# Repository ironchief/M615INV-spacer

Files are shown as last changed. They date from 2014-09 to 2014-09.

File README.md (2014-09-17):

This is a spacer for the OMAX M615INV Portable Inverted Microscope 40x-400x. ([Amazon], [MicroscopeNet])

The spacer allows tissue flasks and petri dishes to fit on the stage by increasing the distance between the light condensor and the sample stage. You can adjust the height using the OpenSCAD or the Makerbot customizer. The original height is 19mm.

---
## Parts
You can reuse the screws, washers and dowel from the original spacer or purchase additional ones with the links below.

- Washer 
    - M3 Metric DIN 125 18-8 Stainless Steel Flat Washer
    - [McMaster-Carr 93475A210](http://www.mcmaster.com/#93475a210)
- Screw
    - M3 6mm 18-8 Stainless Steel Metric Pan Head Phillips Machine Screw
    - [McMaster-Carr 92000A116](http://www.mcmaster.com/#92000a116)
- Dowel
    - M6 22mm Metric 18-8 Stainless Steel Dowel Pin
    - [McMaster-Carr 91585A161](http://www.mcmaster.com/#91585a161)

## Assembly

Loosen the screw at the base of the light source to remove it from the base. Then unscrew the two philips head screws that attach the spacer to the battery case. Reassemble with your printed spacer.

## Files
The OpenScad and STL files can be found on [Github]. Please feel free to make fixes, issues and submit pull requests.

[Amazon]: http://www.amazon.com/OMAX-40X-400X-Portable-Monocular-Microscope/dp/B004EBEYZS
[MicroscopeNet]: http://www.microscopenet.com/40x400x-portable-inverted-microscope-p-8917.html
[Github]: https://github.com/ironchief/M615INV-spacer

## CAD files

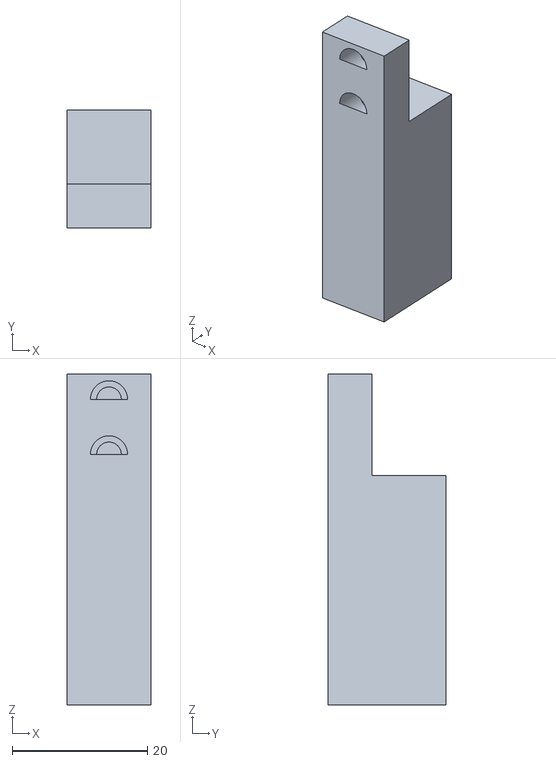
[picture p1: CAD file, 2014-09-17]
spacer.stl
12.5 x 17.5 x 49.0

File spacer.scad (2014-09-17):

// units in millimeters
//


clearance = 30; // [8:50]
//original spacer has 19 mm of clearance
// flask is 25.3mm high

/* [Hidden] */

resolution = 50;
width = 12.5;
depth = 17.5;

cut_height = 15;
cut_depth = 11;
cut_width = width;

microscope_lens = 4;

height = cut_height + clearance + microscope_lens; // original 38 mm

screw_distance = 8.15; // 11.65 and 4.65
screw_diameter = 5.5;
screw_inner_diameter = 3.65;
screw_depth = 5;

peg_diameter = 6.5;
peg_height = 11.6;
peg_distance_front = 6.6+peg_diameter/2;
//6.77 diameter 2.65

module body() {
    difference() {
        cube([width, depth, height], center = false);
        translate([0, depth-cut_depth, height-cut_height])
            cube([cut_width, cut_depth, cut_height], center = false);
        screws();
        translate([0, 0, -screw_distance]) screws();
        peg();
    }
}
module screws() {
    translate([width/2, 0, -screw_diameter/2+height-1]){
        rotate([-90, 0, 0]){
            cylinder(h = screw_depth, d = screw_diameter, $fn = resolution);
            cylinder(h = depth-cut_depth, d = screw_inner_diameter, $fn = resolution);
        }
    }
}

module peg() {
    translate([width/2, peg_distance_front, 0])
    cylinder(h = peg_height,d = peg_diameter , center=false, $fn = resolution);
}
body();
